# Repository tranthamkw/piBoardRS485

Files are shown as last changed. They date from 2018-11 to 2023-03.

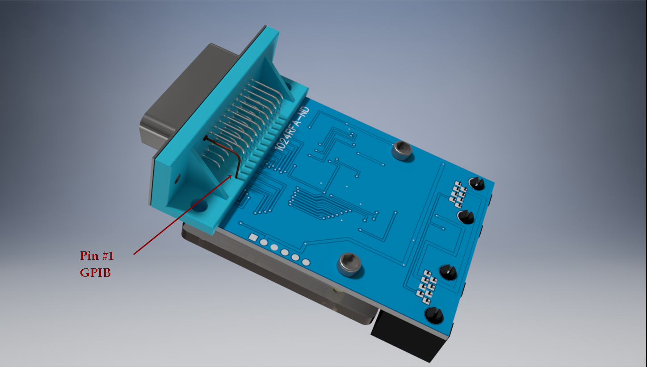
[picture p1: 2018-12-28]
GuestBoards/GPIB_Bridge/GPIB_Fmale_bottomview_Assembly.png

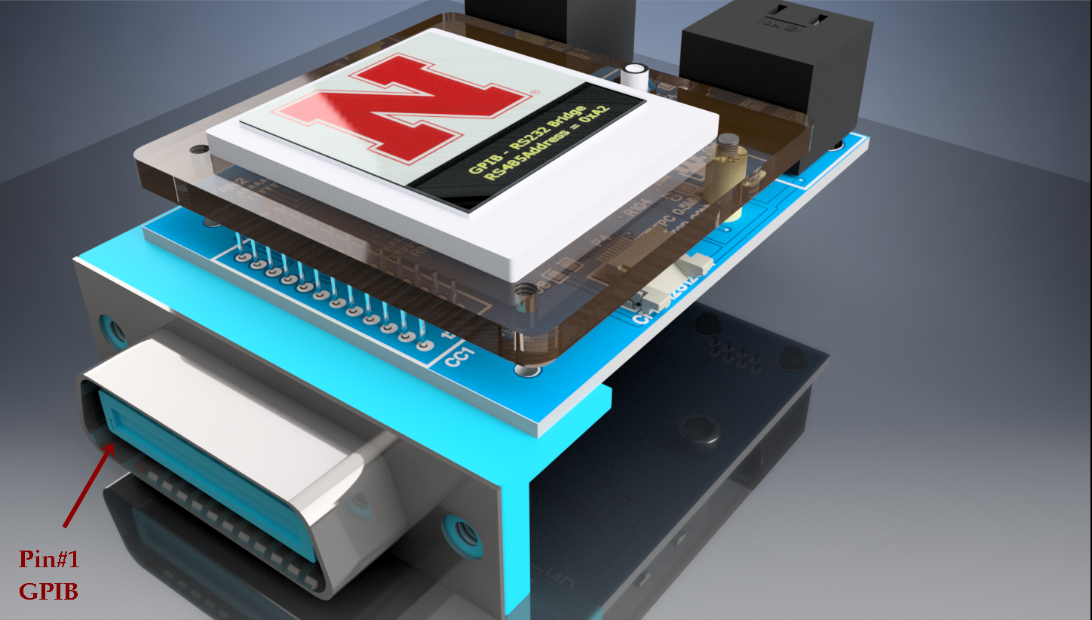
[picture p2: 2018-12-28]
GuestBoards/GPIB_Bridge/GPIB_Fmale_TOPview_Assembly.png

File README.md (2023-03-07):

# piBoardRS485
This repository provides the details of how to build a custom DAQ system based on the RS-485 communication protocol. The primary advantage to the RS-485 protocol is that it allows multiple devices to operate on a single communication line, and that single communication line is the commonly available ethernet cord. This line interfaces with other commonly used communciation standards and connectors, such as GPIB and RS-232, via custom circuit boards, which can be ordered online using the Gerber files located in this repository.

THe system was originally developed to be controlled by a RaspberryPi, but could work with other devices that support serial communication.

A full overview of the project is given in [the pdf document describing the project](https://github.com/tranthamkw/piBoardRS485/blob/master/PROJECTDESCRIPTIONUniversalDataAcq_RS485_system.pdf).

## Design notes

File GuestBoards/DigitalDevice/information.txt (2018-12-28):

/*

Digial devices:
A) servo control
B) General purpose digital IO
C) stepper motor control

Board is the same for all three devices. Funciton is determined with software. 

The  128x32 OLED display is optional. Devices do not require the display to function. Display functions could be removed from the compiled code. The display is useful for displaying routine information, such as the RS485 address. 

*/

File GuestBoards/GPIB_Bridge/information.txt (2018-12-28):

/*  GPIB bridge documentation

Two board versions:
1. Male GPIB uses connector like Digikey 1024RMA-ND mounted on the TOP side of the board. Note where pin 1 is. This version of the board does not have a pushbutton switch for changing the RS485 address.

2. Female GPIB uses connector like Digikey 1024RFA-ND mounted on the BOTTOM side of the board. Again, note where pin 1 is. This version of the board DOES have a push button. 

Both boards: the GPIB connector interferes with the the left two mounting holes for the plexiglass mounting plane for the LCD. The two right mounting holes are sufficient to hold the plexiglass.

*/

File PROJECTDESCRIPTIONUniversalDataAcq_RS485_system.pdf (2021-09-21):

A low‐cost, universal, open‐source, multi‐device data acquisition system for RS485, RS232,

GPIB, and analog devices.

K.W. Trantham and K.J. Ahrendsen

Abstract

A simple, and low cost computerized data acquisition system is presented. It is based on the

Raspberry Pi and can interface to a variety of new and legacy laboratory instruments. For

compatibility with the most common connection standards used by laboratory instruments

(GPIB, RS232, or analog output), it uses a network of communication bridges based on the

RS485 serial bus.

Introduction and motivation

Automated computer or microprocessor data acquisition (DAQ) systems have been in use for

small scale, “personal” experiments, since the 1970’s [1,2]. There are a number of data

acquisition systems, including both hardware and software, available primarily for Windows‐

based Personal Computers (PCs). Including the cost of the computer itself, these systems can be

quite expensive. Furthermore, such third‐party products are generally proprietary, and the

details of their DAQ systems, such as source‐code or electrical schematics, are not available to

the researcher. Over the last ten years, there has been an emergence of very low cost, single‐

board computers that are broadly open‐source, both in software and hardware.

Originally developed as a means to teach coding, the Raspberry Pi (RasPi) computer has many

general‐purpose input/output connections that make it ideal for laboratory automation tasks.

The RasPi uses an open‐source Linux‐based operating system. Furthermore, the vast majority

of software and hardware developed for the RasPi is also open‐source. However, given that the

RasPi is relatively new platform, there are few solutions available to connect it to stand‐alone

laboratory instruments such as an ammeter or lock‐in amplifier. Often, one has a collection of

operational legacy equipment, with much or all of it being unusable in a RasPi DAQ system

given the variety of connection standards. There are many examples [3‐7] where the RasPi has

found specific use in the research environment, often dedicated to a specific task. Herein we present a method for generally connecting the RasPi to any number of new and legacy

instruments, based on a universal, addressable data bus.

One of the most common laboratory instrumentation interfaces is the General Purpose Interface

Bus (GPIB), which conforms to the IEEE 488.1 standard.[8] This is an eight‐bit parallel bus, with

data management and handshake signals. The bus permits addressing up to 30 different

instruments interconnected to a host controller. This bus was first developed by Hewlett‐

Packard (HP) in the 1960’s and has continued to be the de facto standard in laboratory

instrumentation connectivity. To be used with a host computer (such as a PC) an interface card

must be installed. Data acquisition software can be written in native compiled languages, or in

graphical development environments such as LabView[9] or TracerDAQ[10]. Unfortunately, a

commercial solution does not exist to connect a Raspi to the GPIB. A new circuit directly

interfacing the Raspi to the GPIB was considered in the development of our data acquisition

system, but abandoned after considering other instrument connectivity issues.

Newer laboratory equipment may include a GPIB connection, but are more likely to include a

Universal Serial Bus (USB), or an RS232 serial connection. Developing software to communicate

over the USB to third party devices is problematic as special, proprietary drivers are often

required and may not be generally available. This became apparent in our group when trying

to interface to a HighFinesse Model WS‐6 wavemeter. The RS232 serial bus lends itself to

development of locally‐authored software as manufacturers will generally publish command

codes needed to operate their instrument. From an electronics point of view, interfacing the

Raspi to a RS232 bus is straightforward. However the RS232 bus is not addressable and permits

only one device to be connected to the DAQ computer at a time.

Given the diminishing use of GPIB [11] and the limitations of the RS232 bus, we consider the

RS485 serial communication bus. The RS485 bus, standardized in 1998 [12], is also a serial bus

like the RS232. However, the RS485 bus allows multiple devices to be on the same network.

Many modern industrial controls employ the RS485 bus, and its use is becoming more popular

in research settings[13‐17]. Herein we show how the RS485 bus can be used as an alternative,

universal instrumentation connection scheme for laboratory apparatuses. We show how to connect multiple legacy RS232 devices or GPIB devices with a communication bridge circuit. In

developing this bus, it was realized that other, simple interface devices could also be

constructed to expand the measurement and control capability of the laboratory data

acquisition computer.

The RS485 Bus as a Universal Data Bus

The RS485 communication standard defines potentials to represent logic states differently than

do the RS232 systems. Instead of dedicated “transmit” and “receive” potentials measured

relative to ground (three wires) as used in RS232, a version of the RS485 standard uses only two

wires with floating potentials not necessarily referenced to ground. Convention identifies the

two wires and associated potentials as A and B, and VA and VB respectively. Logic states are

determined by the potential difference between wire A and wire B; i.e the state equals the

difference VA ‐ VB. For example, if the difference is greater than zero this represents a logic 0,

and if it is less than zero it represents a logic 1. The advantage this scheme has over RS232

communications is that it is less susceptible to induced noise and completely immune to ground

loops. As a result, RS485 connecting cables can be longer than those for RS232.

To manage transmit and receive functions on the RS485 bus with only two wires, one must

adopt a half‐duplex communication approach. With this, all devices on the bus are by default

“listening” (receiving) with a very large Thevenin impedance seen at the A and B terminals.

Only one device on the bus can transmit at a time. The data conversation is initiated by a “host”

device such as the data acquisition computer. All other devices are then identified as “guest”

devices. In transmit mode, the host device has a very small equivalent Thevenin resistance and

is able to impose the appropriate potentials. The communication information must include an

address so that the appropriate guest device knows to respond when the host device has

completed transmission. After sending a message to the bus, the host enters a high impedance

state (receive mode) and awaits a response from the addressed guest device. The addressed

guest device, in turn, responds by transmitting data on the bus. Thus, the RS485 is an

addressable serial bus, in which there can be many guest devices attached to one host device.

The general architecture of the RS485 serial bus for this application is outlined in Figure 1. Since

the guest devices also require power to operate, +12V and ground are provided along with the

RS485 signals A and B. The electrical‐network connection between devices is simple parallel,

meaning that the network topology can be linear or forked. The RS485 standard does not

specify a physical connector. An RJ‐45 connector is used here, allowing up to eight independent

connections, however only two are used for communication and four more for power (two

wires for +12V and two wires for power ground). Since RJ‐45 is the physical connection

standard for Ethernet, a unique physical connector for this application would prevent

accidental connection of this bus to the Ethernet. However, this connection standard was

selected given the general availability of short “Ethernet cables” and the relatively low cost of

printed‐circuit‐board (PCB) mounted RJ‐45 connectors. The RS485 bus presented here should

not be plugged into an Ethernet connection.

The RS485 standard also does not specify how data is encoded. In this application, data is

encoded using a modified form of the Modbus protocol[18]. This specification outlines the

format of transmitting data, which includes a device address. Most importantly, the protocol

specifies a “cycle‐redundancy‐check” (CRC) to be appended at the end of each transmission.

The CRC is two bytes of data calculated based on the original message and is checked by the

receiver to ensure that there was not an error in transmission. When a guest device responds, in

addition to appending an appropriate CRC, its address is also transmitted so that the host

device can confirm that the correct device responded. Details of the data transmitted over the

RS485 bus are discussed below.

In the present application, there are two basic types of guest devices used. The first type is a

“bridge” device and there are two different versions. The first version is a RS485 to RS232

bridge. This circuit is different from commercially available RS232/RS485 converters, which

typically only modify voltage levels. The device presented here permits addressable

communication with an otherwise non‐addressable RS232 device. In this way, multiple RS232

enabled devices can be controlled with one host device. The second bridge device is a RS485 to

GPIB bridge. This permits a communication interface between the serial RS485 bus and parallel

GPIB bus. The second type of guest device presented is a variety of “general purpose” units

intended to perform simple measurement or manipulation tasks. All of these guest devices and

the host device, which attaches to a RasPi, is described in detail below.

Circuit Descriptions

All guest devices share required common elements in their circuitry. A schematic of these

elements is shown in Figure 2. Each device has two RJ‐45 connectors so that the bus may be

extended to more devices. As shown, pin connections 1 and 2 of the RJ‐45 carry the RS485

signals B and A respectively. Pins 7 and 8 deliver +12V power, with power ground on pins 3

and 4. Pins 5 and 6 are unused, and are tied together. A NCP117ST05T3G voltage regulator

(U2) provides regulated +5V for the guest device. The µMAX485 integrated circuit (U4) is a

data transceiver and provides the necessary electrical translation from RS485 differential

potentials A and B to the +5V, ground referenced transistor‐transistor‐logic (TTL) signals and

vice‐versa. Digital connection RE/DE of U4 determines the mode of communication. When

RE/DE is true, the device is in transmit mode, translating digital TTL level signals at input

UART_TX1 to the appropriate differential signals at A and B. When RE/DE is logical false, the

device is in receive mode and TTL data is provided to digital connection UART_RX1.

Momentary switch SW1 and resistor R2 provide a means to reprogram the device’s address.

This will be discussed further below.

All of the guest devices presented use a Microchip microcontroller (a “PIC”). The development

environment “MPLAB” is available at no cost from the manufacturer. The PIC is programmed

using a PICKIT4 programmer.[19] This low‐cost device connects to the guest board through the

In Circuit Serial Programming (ICSP) connection P1 as shown in Figure 2. Once the PIC is

programmed, the programmer is removed and the code remains on the microprocessor

indefinitely.

All guest devices share optional circuitry for displaying information locally, as shown in Figure

3. The RS232 and GPIB bridge devices use a 128x128 TFT display while all other general

purpose guest devices use a 128x32 OLED display. The displays chief purpose is to show the

user their unique RS485 address when turned on. Optionally, they can provide debugging information, such as the messages being carried from one bus to another as in the case for the

bridge devices. Only one connector and its associated display is used for a given device, but

both are shown in Figure 3. Both displays operate with +3.3V digital signals, and the circuitry

shown translates between this and the +5V logic used by the microcontroller of each device.

Dual transistor package Q101 contains two BSS138 field effect transistors. The operation of this

circuit as a logic level translation circuit is described in reference [20].

The RS485 to RS232 bridge circuit is shown in Figure 4. The indicated ports in Figure 4 connect

to the ports of the same name shown in Figures 2 and 3. The microcontroller U1 is a PIC

18F46K22 whose programming determines the overall behavior of the device. The code used on

all devices is freely available [21]. The 18F46K22 has two Universal Asynchronous Receive and

Transmit (UART) modules. The first UART module is connected to U4 (µMAX485) of Figure 2

and communicates with the RS485 bus. The second UART module is connected to U3

(MAX232) and communicates with the RS232 bus. As the female DB9 is commonly used on the

instruments that support RS232 communication, connector P3 in Figure 4 is a male DB9

intended to plug into the back of the instrument. Essentially, this bridge device listens on the

RS485 bus for data specifically addressed for it. When properly addressed through the RS485

bus, it strips out RS485 and Modbus specific data and transmits the intended message (usually

ASCII text) to the connected instrument via the RS232 bus. The bridge waits for a certain period

and transmits any data returned from the instrument back through the RS485 bus with

appropriate Modbus encoding data. Printed circuit Gerber files are also available [21].

The RS485 to GPIB bridge circuit is shown in Figure 5 and is similar in function to the RS232

bridge. It accepts properly addressed and encoded messages intended for a GPIB instrument,

passes along the instrument‐specific instructions, and returns any data passed back from the

instrument. This circuit only uses one UART of the microcontroller for the RS485 bus. The

GPIB communication is handled manually through the digital data Port A for reading and

writing data to the GPIB bus, while digital port D handles GPIB bus management signals per

IEEE 488.1. A full description of how the GPIB bus operates can be found in reference [22].

Briefly, the digital signals in the GPIB bus are “active low” meaning that a given signal is not true until the signal is near ground level. With many possible instruments on the bus, the signal

line will not be sensed low until all instruments have pulled the line low. The resistor networks

shown in Figure 5 permit the microcontroller to both sense the level of a given signal and

transmit data when needed.

Since the PIC microcontrollers have software‐controllable digital input/output ports as well as

analog input ports, we realized that RS485 devices could be constructed for simple remote data

acquisition and control tasks. Placing data acquisition and control tasks in a remote device frees

the main computer for other tasks. An example task that is better removed from the host

computer is the provision of regular step pulses to control a stepper motor. Because the RaspPi

runs a multitasking Linux operating system, like Windows on a PC, microprocessor time

dedicated to user code can be variable. This makes providing regularly timed pulses difficult.

A PIC microcontroller, on the other hand, runs dedicated code and timing functions can be

more precisely controlled with on‐chip counter‐timer circuits.

The electrical schematic for a general purpose RS485 digital guest device is shown in Figure 6.

This device can be programmed to control two servomotors, control one stepper motor, or

simply be a general‐purpose digital input/output device. Depending upon how the PIC is

programmed, output ports RA5 and RA4 of the PIC provide digital signals to control two

servomotors. Alternatively, these pins can output the pulse and clock signals for one stepper‐

motor, or, along with RC3 and RB4, can be used for general digital input/output (I/O) tasks.

The circuit is based on the PIC16F690 microcontroller. Like the PIC18F18K22, this

microcontroller is inexpensive and readily available. It has three 8‐bit general purpose digital

I/O ports, eight 10‐bit analog to digital converters (ADCs), two timers, two comparators, and

one UART. Many of these functions are tied to the same pin. For example, pin 12 of the

PIC16F690 is internally connected to digital port B bit 5, analog to digital converter channel 11,

and the receive connection for the UART. Therefore, the use of the pin must be configured in

software with the intended function. This means that other possible functions tied to a given

pin cannot be used at the same time. Connectors J4 and J5 provide power and signals for

conventional servo connectors. If this digital guest‐device is used as a servo controller, a separate voltage regulator U7 provides dedicated power for servos. Although the servos and

microcontroller circuit both require +5V to operate, the higher current drawn from the servos

can cause the supply voltage to fluctuate such that the microcontroller will reset. This generally

leads to erratic behavior.

Another use of the PIC16F690 as a remote RS485 guest device is to measure analog signals.

Some legacy equipment will only have an analog output as the remote sensing method. Figure

7 shows the schematic for a four‐input analog RS485 analog guest device. The analog input

section has a simple resistor and Zener diode network for limiting the input voltage to +5.1V

relative to ground as measured by the microcontroller. If the device needs to measure a

different voltage range, or bipolar voltages, then additional analog voltage conditioning circuits

can be added. The PIC16F690 uses a 10‐bit analog to digital converter (ADC). This resolution is

sufficient for many applications, however there are a variety of other PIC microcontrollers that

have better resolution or pre‐processing options such as averaging (see, e.g. the PIC18F27K42).

Finally, we present the circuitry for the host computer in Figure 8. The host computer is a

Rasberry Pi model 2 and connects to the circuit via connector P1. The circuitry is similar to the

guest devices in that a µMAX485 integrated circuit translates +5V TTL logic signals to RS485

potentials. The networks around Q1 and Q2 provide logic level shifting between the +5V

system of the µMAX485 and the +3.3V logic of the RasPi. There are two extra resistors attached

to the A and B wires of the RS485 bus. The A and B wires are completely floating and their

potentials could possibly drift outside of the 0 to +5V range used to power U4. These resistors

provide a minuscule amount of biasing current to prevent this. The main difference between

the RasPi host device and the other devices shown in previous figures is the software. The host

computer always initiates a data transfer by first addressing the intended device and then

awaiting a response. Although only two RJ‐45 connectors are shown in Figure 8, the user can

add as many connectors as needed. The RasPi computer can also interface to other devices

through the unused circuit node tags shown in Figure 8, e.g. CE0, MOSI, and WPi25. These are

not relevant to the RS485 host controller application and will not be discussed.

Data Format

The serial data format for all devices follows a modified form of the Modbus protocol. The

order of each 8‐bit byte has significance. The first byte transmitted by the host is the unique

RS485 address of the device which is intended to reply. This is followed by a control byte;

examples include 0x03 for reading from a register or 0x06 for writing to a register. The next two

bytes indicate which register to read from or write to. In the case of writing, the next two bytes

indicate what value to write. The last two bytes are the low and high order CRC bytes. As an

example, the byte stream

0xA1 0x03 | 0xF0 0xF2 <CRC_l> | <CRC_h>

transmitted by the host is intended for device number 0xA1 (decimal 161) and is requesting to

read data from register 0xF0F2. The host then goes into listen mode and awaits a response.

Only guest device 0xA1 will respond. The byte order of the response also has the address first,

and the second, control byte is echoed. In the case of writing to a register, the entire message is

typically echoed back. In the case of reading from a register, the third byte indicates the

number of bytes of data to follow in the stream. The low and high order CRC bytes are

transmitted last. Thus, continuing with the above example, the device might respond with five

bytes of ASCII encoded data for “HELLO” as,

0xA1 0x03 | 0x05 | 0x48 | 0x45 | 0x4C 0x4C 0x4F <CRC_l> | <CRC_h>.

All devices on the RS485 network employ a means of changing the RS485 address of the guest

device. This is necessary since all devices on the network must have a unique address between

0x00 and 0xFF. When the microcontroller is first programmed, the address is indeterminate.

All guest devices have an “ADDRESS” port to the microprocessor and associated momentary

switch. When the switch is held closed and a properly encoded message is sent at the same

time, the guest device will remember the address used in the message as its own and act on the

message. When the switch is released, this new address is permanently saved even if power is

removed from the device. A second method of changing the address is provided by software.

By sending the proper information through the RS485 bus to the correct register of the device,

the address can be changed as well.

An Example Use

We have adapted the digital host device to control laser paths on an optical table. It is a

straight‐forward procedure to connect a small flag to a servo. This allows the DAQ system to

block, or unblock a laser beam as desired. Further, a servo can be connected to a flip mirror for

controlling the laser beam direction. Referring to Figure 9, a small “fork” (item 4) is mounted

on a servo motor. An adjustable mirror mount (item2) [Thorlabs KM100] is mounted to a flip

mount adapter (1) [Thorlabs FM90]. The servo is mounted so that its axis is concentric with the

axis of the flip mount adapter. Finally, a protruding screw (item 3) in the mirror mount fits

between the tines of the fork.

Conclusion

We have presented a universal data acquisition bus to network a Linux‐based Raspberry Pi to a

variety of laboratory equipment. With communication bridges and general purpose RS485

devices, this system has been tested with a variety of devices. We have also developed a novel,

remote controlled flip‐mirror based on the general‐purpose digital device. Table 1 shows a

complete list of commercial equipment tested with our system and the mode of interface to the

RS485 bus. At any given time, all of this equipment can be connected to the bus and DAQ

computer.

Equipment | Mode of connection to RS485 bus
Keithley Model 485 Picoammeter | GPIB bridge
Keithley Model 617 Electrometer | GPIB bridge
Vortex Laser Model 6000 | RS232 bridge
Sacher Laser Head Controller PilotPC 500 | RS232 bridge
Sacher Tapered Amp Controller PilotPC 4000 | RS232 bridge
Omega Model CN7800 Temperature Controller | RS232 bridge
B&K Model 1696 power supply* | RS232 bridge
SRS Model SR830 Digital Lock‐in Amplifier | RS232 bridge or GPIB bridge
HighFinesse Model WS‐6 Wavemeter* | RS232 bridge
Grandville Phillips Model 307 ion gauge and Convectron gauge controller | Analog input guest device
FLUKE 8840 Multimeter | GPIB bridge
Sorensen 120‐0.5 power supply | GPIB bridge

Table 1. A list of commercial laboratory equipment tested and used with the described

RS485bus. Items marked with an asterisk have special notes, see text.

Interfacing to the Model WS‐6 wavemeter requires a special note. The hardware for this device

is controlled through the USB port with proprietary software written for the PC/Windows. The

software has a configuration option to continuously broadcast the wavemeter’s data through

the RS232 serial port of the PC. The above RS485 to RS232 bridge was adapted with a female

DB9 connector and wiring the Rx and Tx connections to the appropriate pins. The bridge was

reprogrammed to read two sequences of the byte stream from the PC computer since, at any

given moment when the data was requested from the DAQ host, the first data sequence could

be incomplete. The B&K Model 1696 power supply can also connect directly through RS485.

However, its mode of communication is ASCII text only. To preserve the purity of the

communication on the RS485 bus and to avoid possible data errors with other devices using the

Modbus data format, the RS232 bridge is used with this power supply.

The components used on each device and the host computer are relatively inexpensive. It is

straight‐forward to connect the RasPi to the RS485 bus since TTL‐level serial Rx and Tx

connections are readily available. This universal system of connecting multiple devices can be

extended to using a PC as the DAQ. In this extension, however, a translation circuit such as a

RS232 to RS485 bridge would need to be employed as TTL connections are not available on the

PC.

Acknowledgements

This work was supported by the NSF through Awards PHY‐1505794 and PHY‐1806771.

References

1. D.W. Taylor, Review of Scientific Instruments 49, 1551 (1978).
2. Douglas Whiting, Review of Scientific Instruments 55, 1157 (1984).
3. Alfredo Benítez, Ulises Santiago, John E. Sanchez, and Arturo Ponce, Review of Scientific

Instruments 89, 013702 (2018).

4. F. Arnold, I. DeMallie, L. Florence, and D. O. Kashinski, Review of Scientific Instruments 86,

035112 (2015).

5. James Keaveney, Review of Scientific Instruments 89, 035114 (2018).
6. Matthew G. Street, Cristin G. Welle, and Pavel A. Takmakov, Review of Scientific

Instruments 89, 094301 (2018).

7. N. B. Clayburn, K. W. Trantham, M. Dunn, and T. J. Gay, Review of Scientific Instruments 87,

124903 (2016).

8. IEEE Standard Digital Interface for Programmable Instrumentation, Institute of Electrical and

Electronics Engineers, 1987, ISBN 0‐471‐62222‐2,

9. See www.ni.com/labview for LabVIEW.
10. See https://www.mccdaq.com for TracerDaQ.

11 J Ryland ‐ Autotestcon, 2005. IEEE, 2005 ‐ ieeexplore.ieee.org, DOI:

10.1109/AUTEST.2005.1609228

12. Electronic Industries Alliance standard ANSI/TIA/EIA‐485‐A‐1998.
13. J. Vega, A. Mollinedo, A. López, L. Pacios, and S. Dormido, Review of Scientific Instruments

68, 963 (1997).

14. A. K. Sanyasi, R. Sugandhi, P. K. Srivastava, Prabhakar Srivastav, and L. M. Awasthi,

Review of Scientific Instruments 89, 055113 (2018).

15. Hui Gao, Qiuping Wang, Weibin Wang, Qinglin Wu, Wentong Chen, Liusi Sheng, and

Yunwu Zhang, Review of Scientific Instruments 72, 3979 (2001)

16. Sanjeev R. Kane, Chander Kant Garg, and R. V. Nandedkar, AIP Conference Proceedings

879, 635 (2007)

17. R. Szplet, P. Kwiatkowski, K. Różyc, Z. Jachna, and T. Sondej, Review of Scientific

Instruments 88, 125101 (2017).

18. http://www.ni.com/white‐paper/7675/en/ for Introduction to Modbus (white paper).
19. See https://www.microchip.com for PICkit programmers and MPLAB software.
20. Phillips AN10441 application note https://www.nxp.com/docs/en/application‐

note/AN10441.pdf

21. Schematics, microcontroller source code, and circuit board Gerber files available at [URL

held pending anonymous peer review] github repository.

22. See http://www.ni.com/white‐paper/3389/en/ for Introduction to GPIB messages (white

paper)

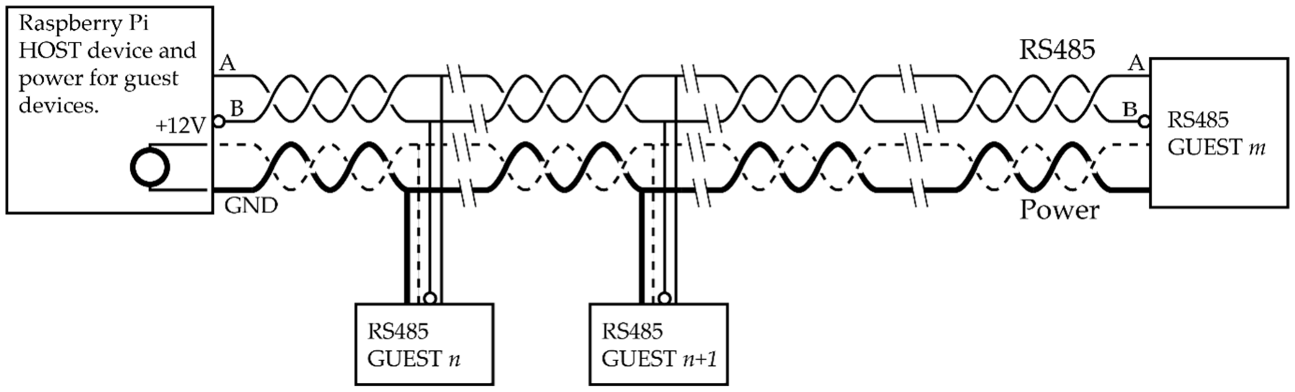
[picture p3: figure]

Figure 1. General architecture of the powered RS485 instrumentation bus.

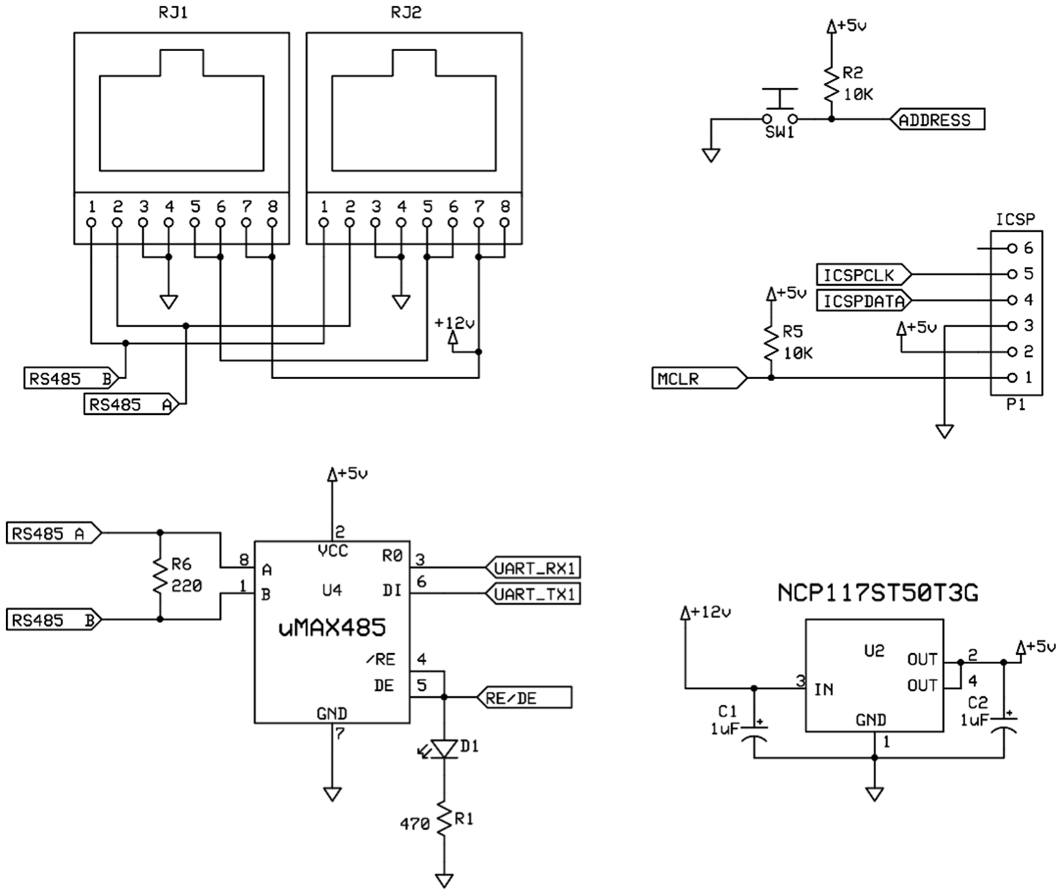
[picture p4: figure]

Figure 2. Schematic of the required common elements found in each guest RS485 device.

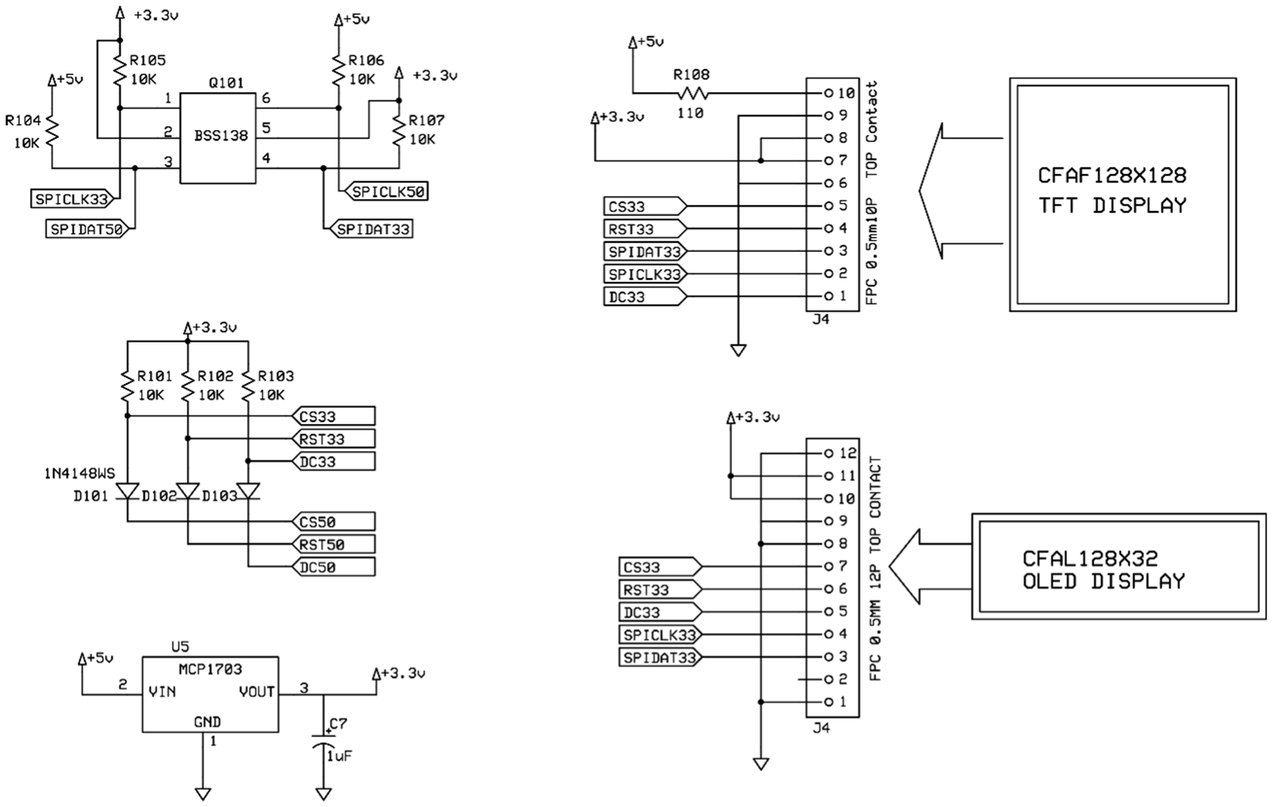
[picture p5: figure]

Figure 3. Schematic of optional display circuitry used on each device. The bridge guest devices

use the 128x128 TFT display, while all other devices use the 128x32 OLED display.

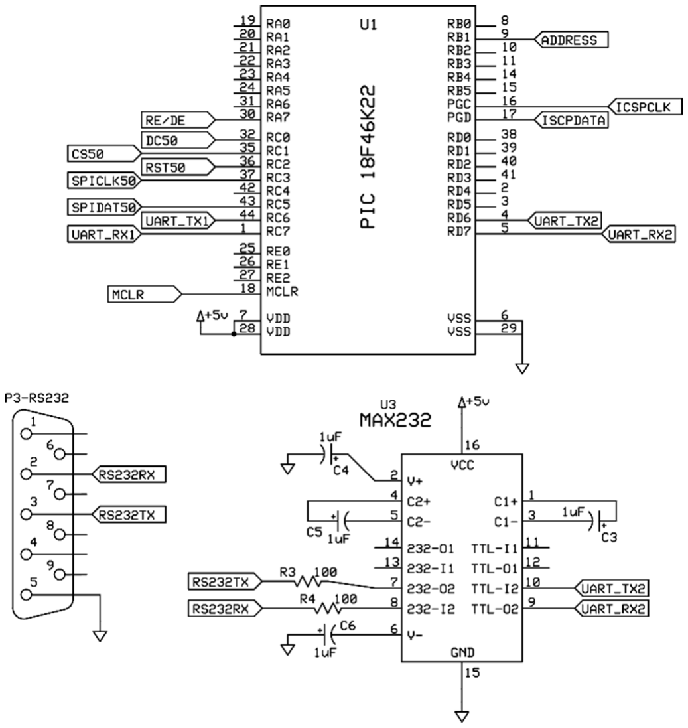
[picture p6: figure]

Figure 4. Schematic of RS485 to RS232 bridge guest device.

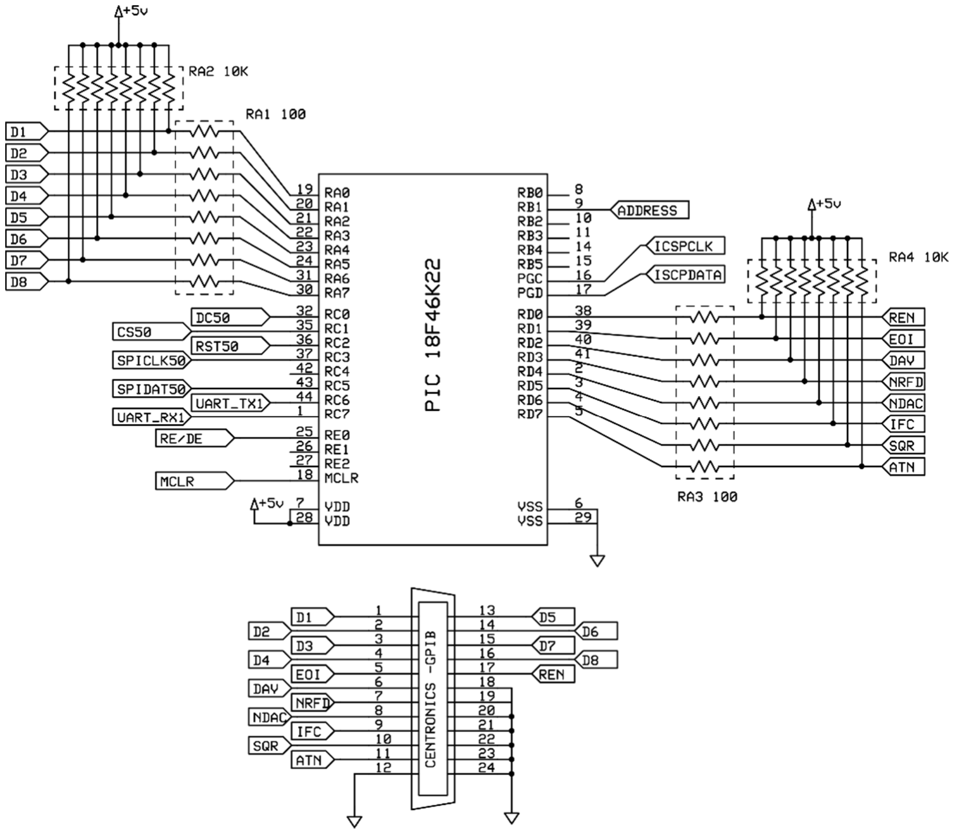
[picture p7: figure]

Figure 5. Schematic of RS485 to GPIB bridge guest device.

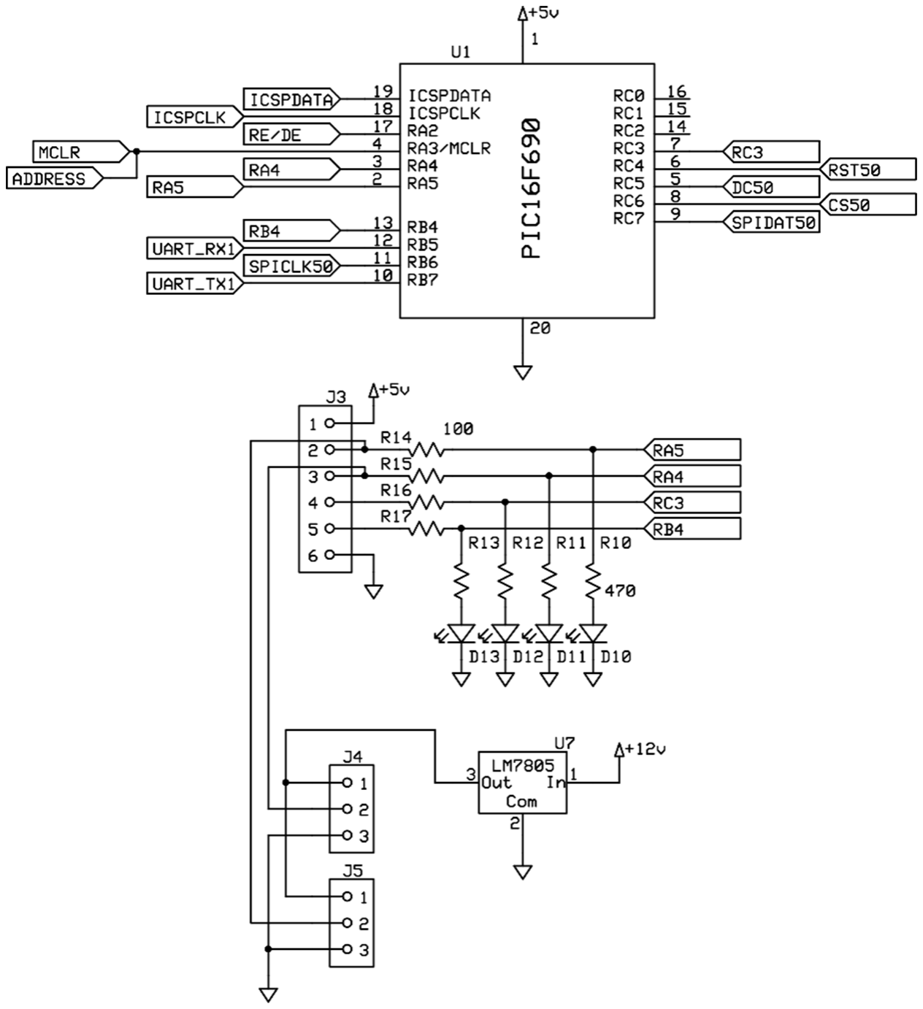
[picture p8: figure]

Figure 6. General‐purpose digital RS485 guest device. With appropriate software, this circuit is

used to control two servomotors, one stepper motor, or provide general digital I/O signals.

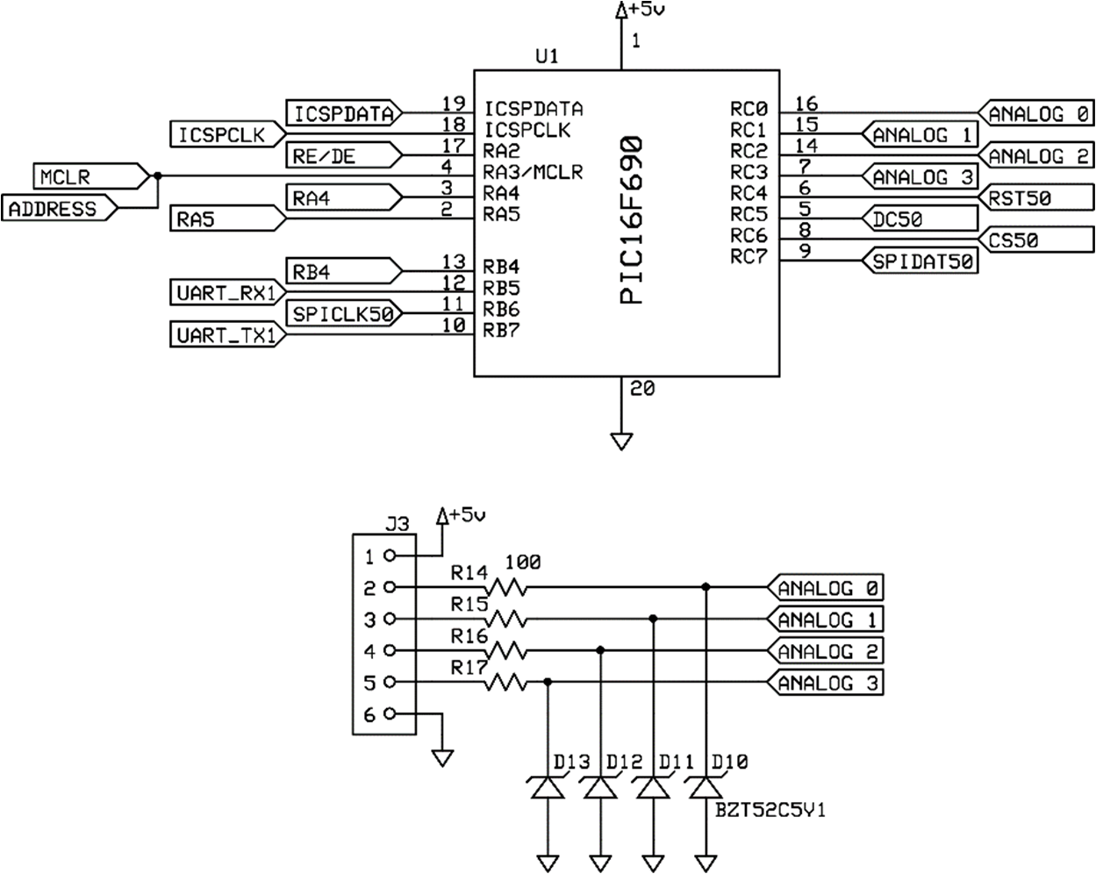
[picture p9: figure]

Figure 7. General‐purpose analog input RS485 guest device.

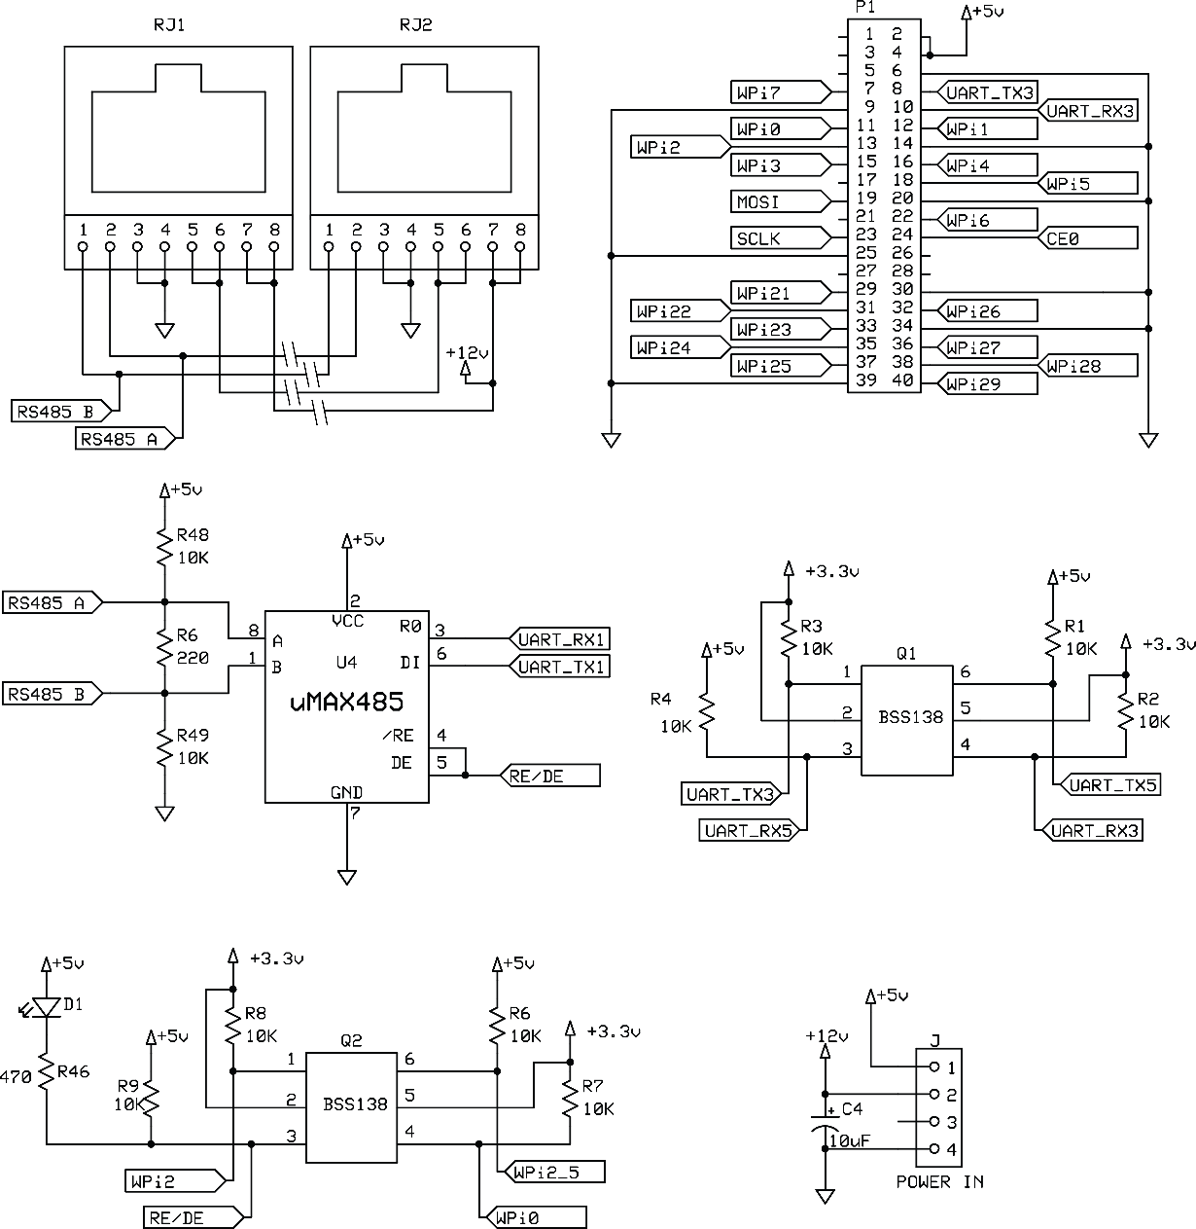
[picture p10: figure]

Figure 8. Circuit for the raspberry Pi RS485 host controller.

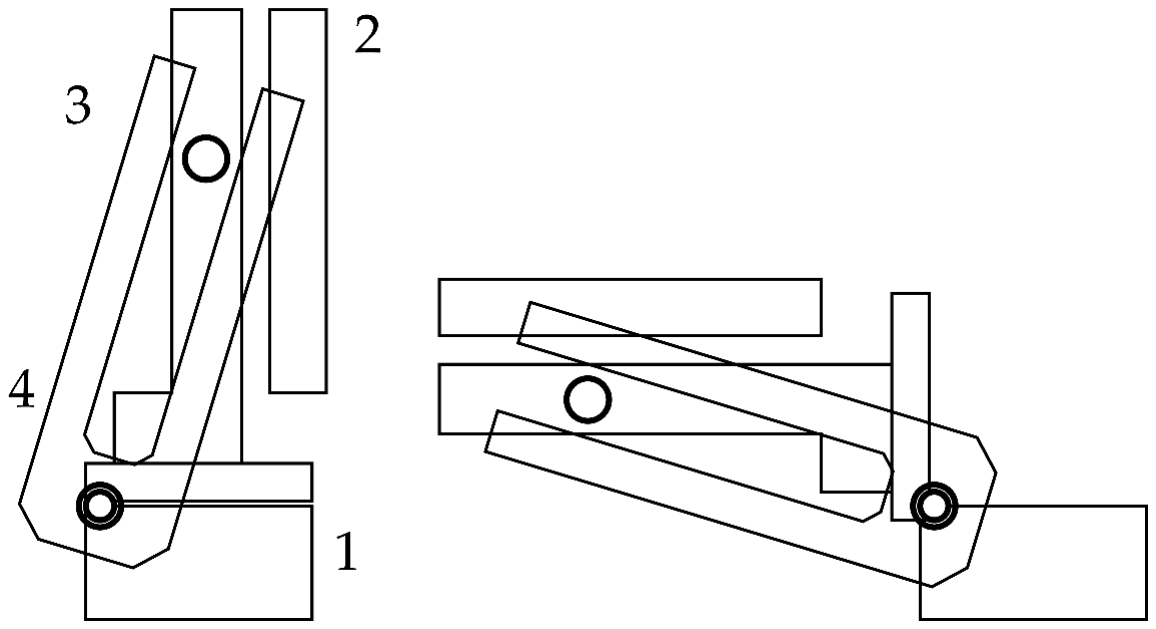
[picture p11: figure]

Figure 9. An automatic flip‐mirror based on the digital servo guest device. A servo (not

shown) is used to change the position of a mirror. See text for numbered item descriptions.

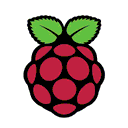
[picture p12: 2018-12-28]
RaspPi128x128.bmp

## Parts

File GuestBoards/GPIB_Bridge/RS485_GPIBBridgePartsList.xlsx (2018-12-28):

Name | Designator | Footprint | Quantity | Supplier | Supplier Part
1uF | C7,C1,C2 | CASE-A_3216 | 3 | https://www.digikey.com | 399-3680-1-ND
GPIB_connector_male | CC1 | 24-p.085" pitch FEMALE | 1 | https://www.digikey.com | 1024RFA-ND | <- with 20181111200508 board
 | CC1 | 24-p.085" pitch MALE | 1 | https://www.digikey.com | 1024RMA-ND
1N4148WS | D101,D102,D103 | SOD-323-F | 3 | https://www.digikey.com | 1N4148WSFSCT-ND
LTST-C170KRKT | LED1 | LED-0805 | 1 | https://www.digikey.com | 475-1278-1-ND
Header-Female-2.54_1x6 | P1 | HDR-6X1/2.54 | 1 | https://www.digikey.com | 732-5339-ND
FPC 0.5MM 10P Pull type H2.0mm Pick up | P4 | FPC-0.5MM-LSSJ-H2.0-10P_TOP | 1 | https://www.digikey.com | HFK110CT-ND
BSS138DW-7-F | Q101 | SC-70-6(SOT-363) | 1 | https://www.digikey.com | BSS138DW-FDICT-ND
470Ω(471) | R1 | 0603' | 1 | https://www.digikey.com | 311-470CRCT-ND
10K | R105,R104,R106,R107,R102,R101,R103 | 0805' | 7 | https://www.digikey.com | 311-10.0KCRCT-ND
120R | R108 | 0805' | 1 | https://www.digikey.com | 311-120CRCT-ND
10K-0805 | R2,R5 | 0805' | 2 | https://www.digikey.com | 311-10.0KCRCT-ND
220R-1206 | R6 | 1206 | 1 | https://www.digikey.com | YAG5046CT-ND
RJ45c | RJ1,RJ2 | RJ45-3.68 | 2 | https://www.digikey.com | 553-2264-ND
ResistorArray100 | RN1, RN3 | RESISITOR_ARRAY_742C163_CTS | 1 | https://www.digikey.com | 742C163101JPCT-ND
ResistorArray10k | RN2,RN4 | RESISITOR_ARRAY_742C163_CTS | 3 | https://www.digikey.com | 742C163103JPCT-ND
SWITCH,6*6*9PLASTIC HEAD,260G, 0.25MM,SMD | SW1 | SMD-6X6X9 | 1 | https://www.digikey.com | EG4356CT-ND
PIC18F46K22-I/PT | U1 | TQFP-44_10X10X08P | 1 | https://www.digikey.com | PIC18F46K22-I/PT-ND
NCP1117ST50T3G | U2 | TO-261-4 | 1 | https://www.digikey.com | NCP1117ST50T3GOSCT-ND
MAX485CUA+ | U4 | UMAX-8 | 1 | https://www.digikey.com | MAX485CUA+-ND
MCP1703AT-3302E/MB 3.3V Regulator | U5 | SOT-89(SOT-89-3) | 1 | https://www.digikey.com | MCP1703AT-3302E/MBCT-ND
128x128 1.45" Full Color TFT LCD Display | *not shown | Mounts external | 1 | https://www.crystalfontz.com | CFAF128128B10145T

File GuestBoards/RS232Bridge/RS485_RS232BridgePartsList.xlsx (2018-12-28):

Name | Designator | Footprint | Quantity | Supplier | Part number
1uF | C1,C2,C3,C4,C5,C6,C7 | CASE-A_3216 | 7 | https://www.digikey.com | 399-3680-1-ND
1N4148WS-E3-08 GP DIODE | D101,D102,D103 | SOD-323-F | 3 | https://www.digikey.com | 1N4148WSFSCT-ND
LTST-C170KRKT | LED1 | LED-0805 | 1 | https://www.digikey.com | 475-1278-1-ND
Header-Female-2.54_1x6 | P1 | HDR-6X1/2.54/rightAngle | 1 | https://www.digikey.com | 732-5339-ND
RS232-DB9 | P3-RS232 | PCB Edge mount | 1 | https://www.digikey.com | 209ME-ND
FPC 0.5MM 10P Pull type H2.0mm TOP | P4 | FPC-0.5MM-LSSJ-H2.0-10P_TOP | 1 | https://www.digikey.com | HFK110CT-ND
BSS138DW-7-F | Q101 | SC-70-6(SOT-363) | 1 | https://www.digikey.com | BSS138DW-FDICT-ND
470R | R1 | 0603 | 1 | https://www.digikey.com | 311-470CRCT-ND
10k | R2,R5,R104,R105,R106,R107,R102,R101,R103 | 0805 | 9 | https://www.digikey.com | 311-10.0KCRCT-ND
120R | R108 | 0805 | 1 | https://www.digikey.com | 311-120CRCT-ND
100R | R3,R4 | 0805 | 2 | https://www.digikey.com | 311-100CRCT-ND
220R | R6 | 1206 | 1 | https://www.digikey.com | YAG5046CT-ND
RJ45c | RJ1,RJ2 | RJ45-3.68 | 2 | https://www.digikey.com | 553-2264-ND
SWITCH,6*6*9PLASTIC HEAD,260G, 0.25MM,SMD | SW1 | SMD-6X6X9 | 1 | https://www.digikey.com | EG4356CT-ND
PIC18F46K22-I/PT | U1 | TQFP-44_10X10X08P | 1 | https://www.digikey.com | PIC18F46K22-I/PT-ND
NCP1117ST50T3G | U2 | TO-261-4 | 1 | https://www.digikey.com | NCP1117ST50T3GOSCT-ND
MAX232ESE+T | U3 | SOIC-16_150MIL | 1 | https://www.digikey.com | 296-14619-1-ND
MAX485CUA+ | U4 | UMAX-8 | 1 | https://www.digikey.com | MAX485CUA+-ND
MCP1703AT-3302E/MB 3.3V Regulator | U5 | SOT-89(SOT-89-3) | 1 | https://www.digikey.com | MCP1703AT-3302E/MBCT-ND
128x128 1.45" Full Color TFT LCD Display | *not shown | Mounts external | 1 | https://www.crystalfontz.com | CFAF128128B10145T

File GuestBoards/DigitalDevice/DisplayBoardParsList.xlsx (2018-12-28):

Name | Designator | Footprint | Quantity | Supplier | Supplier Part
BSS138DW-7-F | Q1 | SC-70-6(SOT-363) | 1 | Digikey | BSS138DW-FDICT-ND
10k-0805 | R1,R2,R3,R4,R5,R6,R7 | 0805' | 7 | Digikey | 311-10.0KCRCT-ND
1N4148WS-E3-08 GP DIODE | D1,D2,D3 | SOD-323-F | 3 | Digikey | 1N4148WSFSCT-ND
MCP1703AT-3302E/MB 3.3V Regulator | U1 | SOT-89(SOT-89-3) | 1 | Digikey | MCP1703AT-3302E/MBCT-ND
1uF | C1 | CASE-A_3216 | 1 | Digikey | 399-3680-1-ND
FPC_0.5MM_12P_rEVERSE | P4 | FPC-0.5MM-LSSJ-H2.0-12P | 1 | Digikey | A100294CT-ND
Header-Female-2.54_1x8 | P1 | HDR-8X1/2.54 | 1 | Digikey | 732-5321-ND
128x32 I2C Graphic OLED Module with ZIF Connector |  |  | 1 | www.crystalfontz.com | CFAL12832D-B

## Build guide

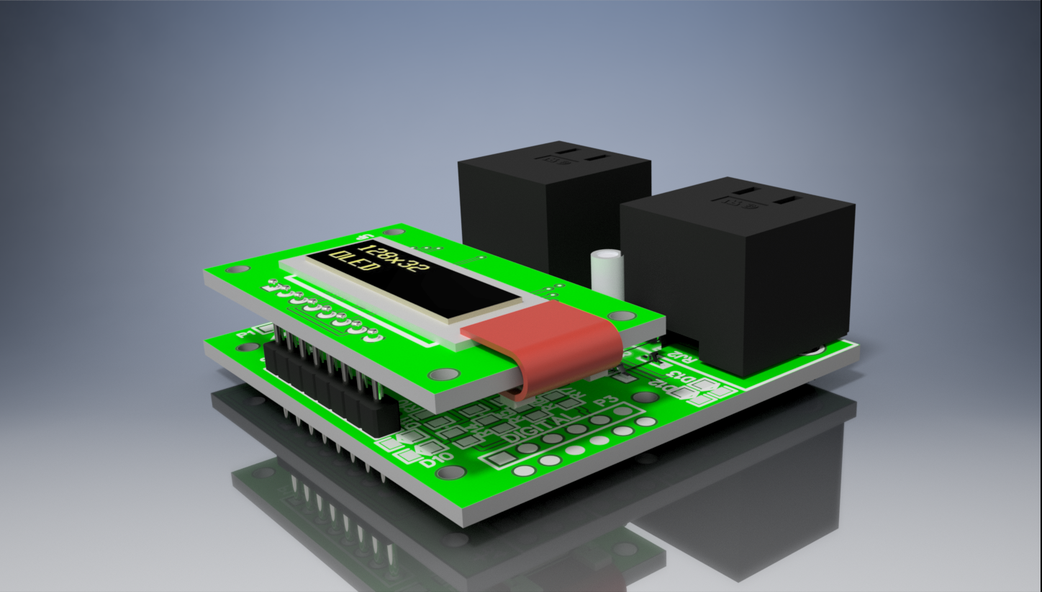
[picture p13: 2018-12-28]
GuestBoards/DigitalDevice/DigitalBoardAssembly.png

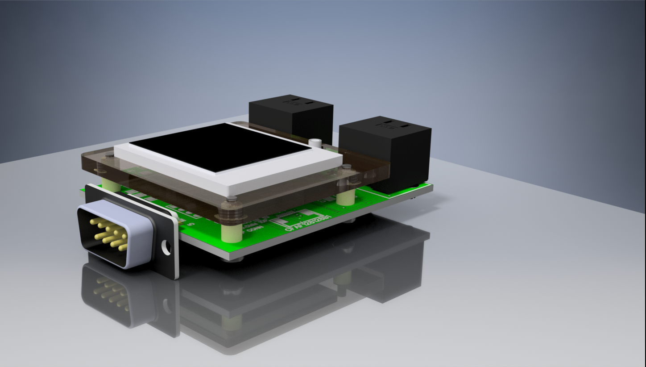
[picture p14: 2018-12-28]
GuestBoards/RS232Bridge/RS232Bridge_assembly.png

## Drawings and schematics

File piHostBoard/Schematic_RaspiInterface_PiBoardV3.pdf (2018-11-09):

+12V +5V
+5V

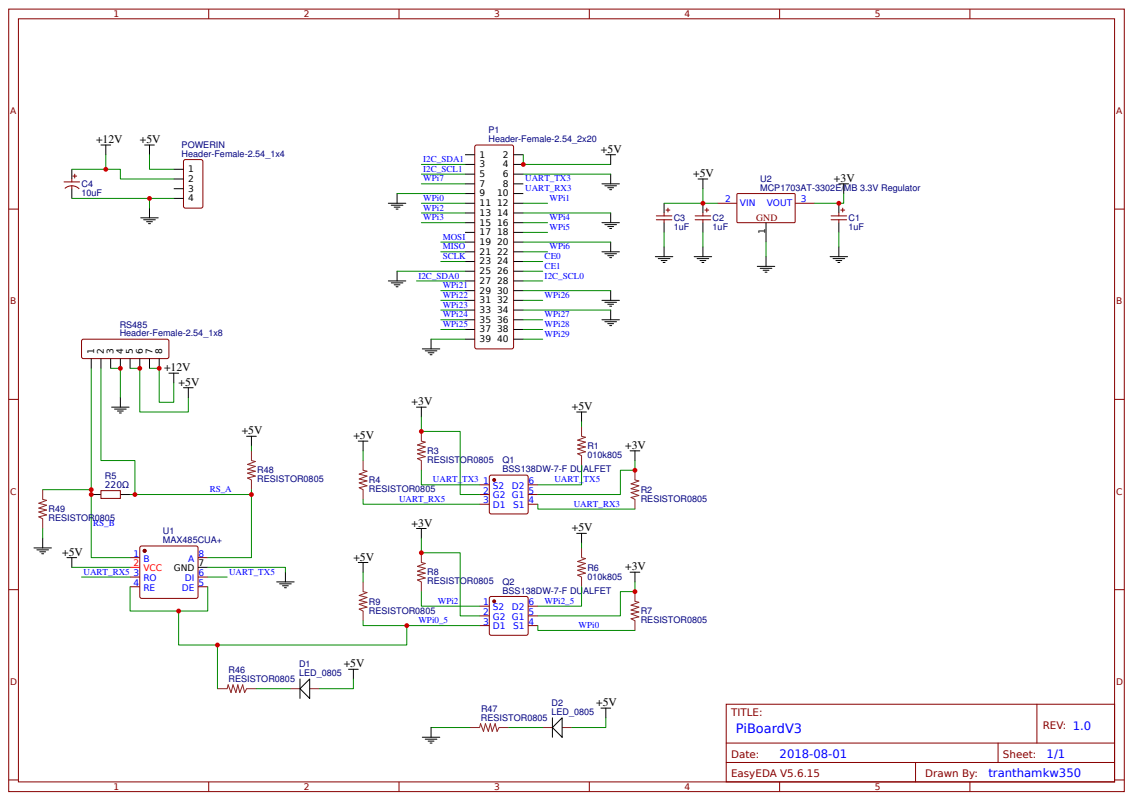
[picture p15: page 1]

+5V

+5V

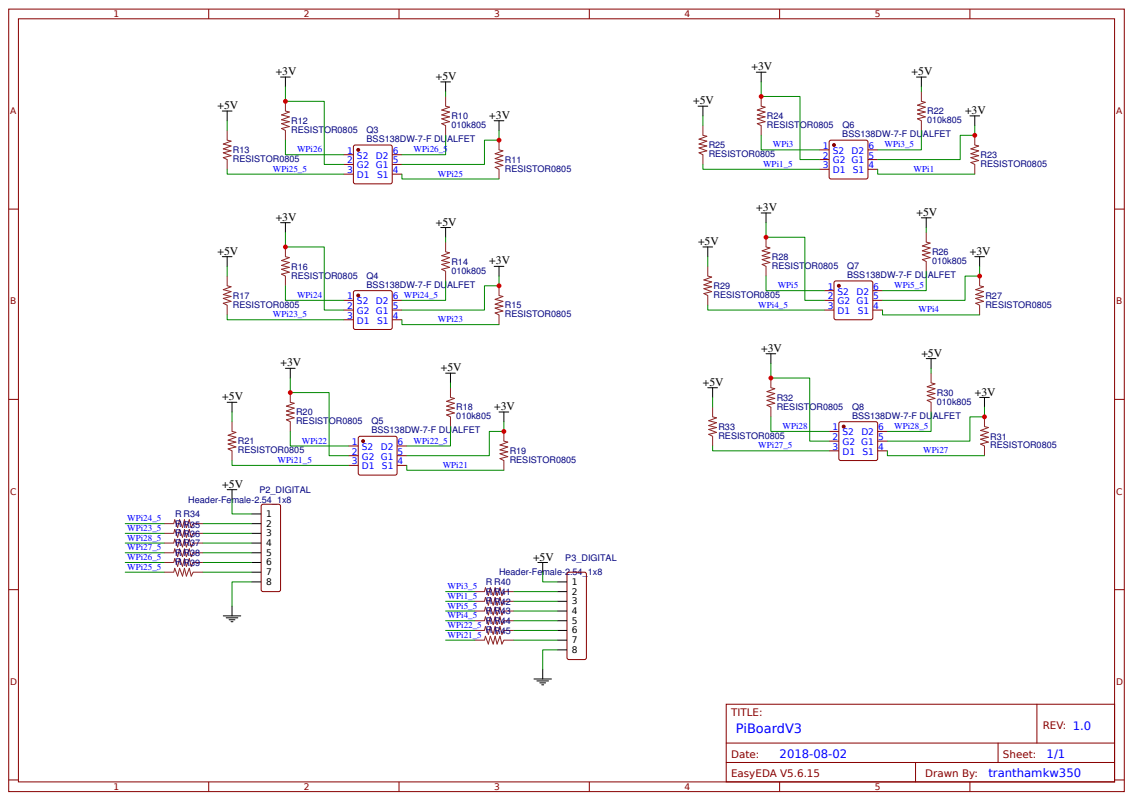
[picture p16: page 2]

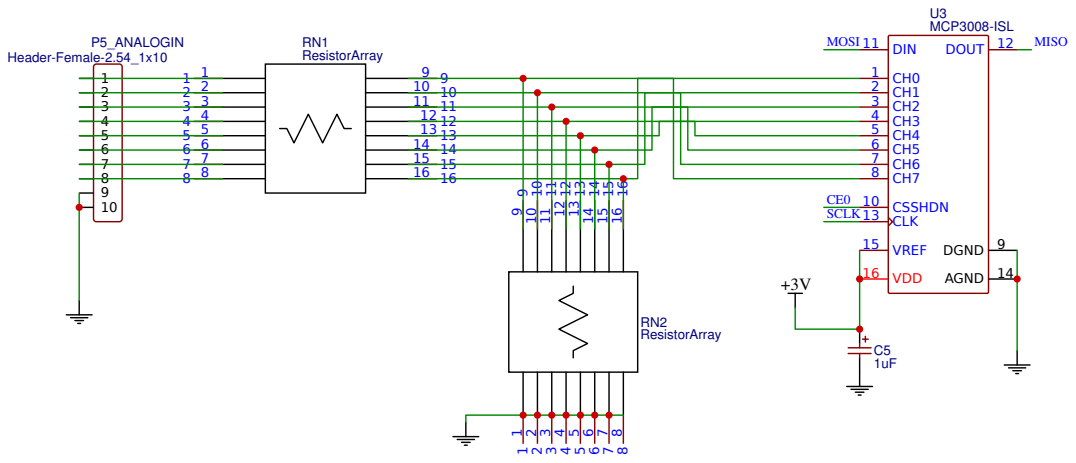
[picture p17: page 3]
TITLE:; New Schematic; REV: 1.0; Date:; Sheet: 1/1; MCP3008-ISL; DGND 9; CSSHDN 10 CLK 13; VREF 15; DIN 11; DOUT 12; AGND 14 VDD 16; Header-Female-2.54_1x10; P5_ANALOGIN; CE0 SCLK; MOSI; MISO; ResistorArray

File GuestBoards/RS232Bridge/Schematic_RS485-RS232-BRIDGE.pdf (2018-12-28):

+5V

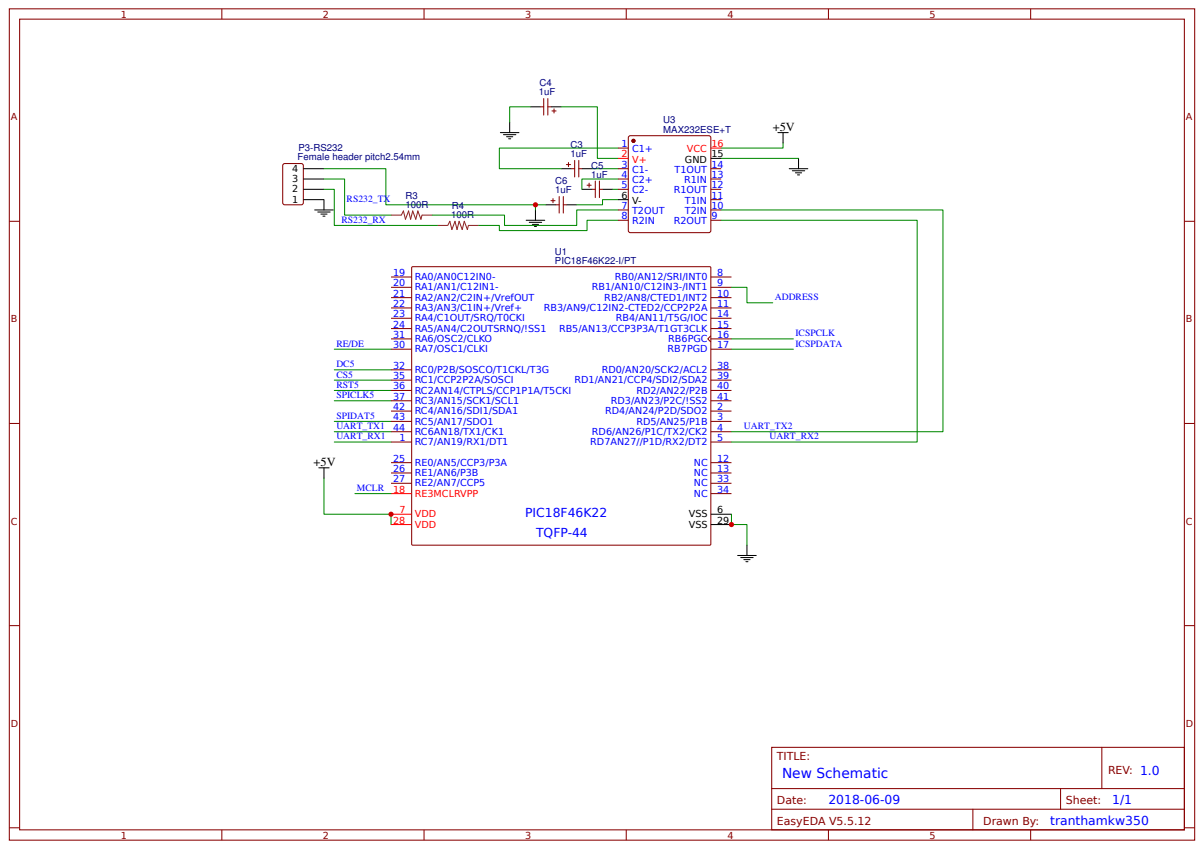
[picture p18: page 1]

+5V
+5V

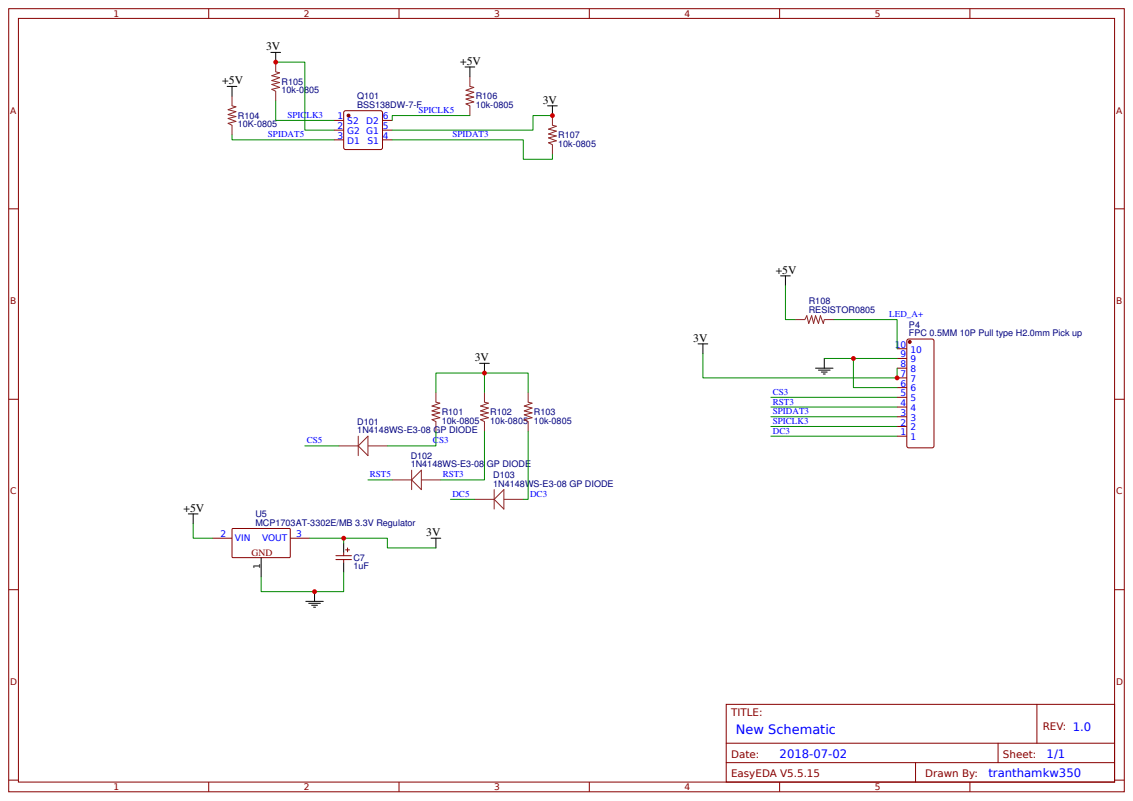
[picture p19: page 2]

+5V

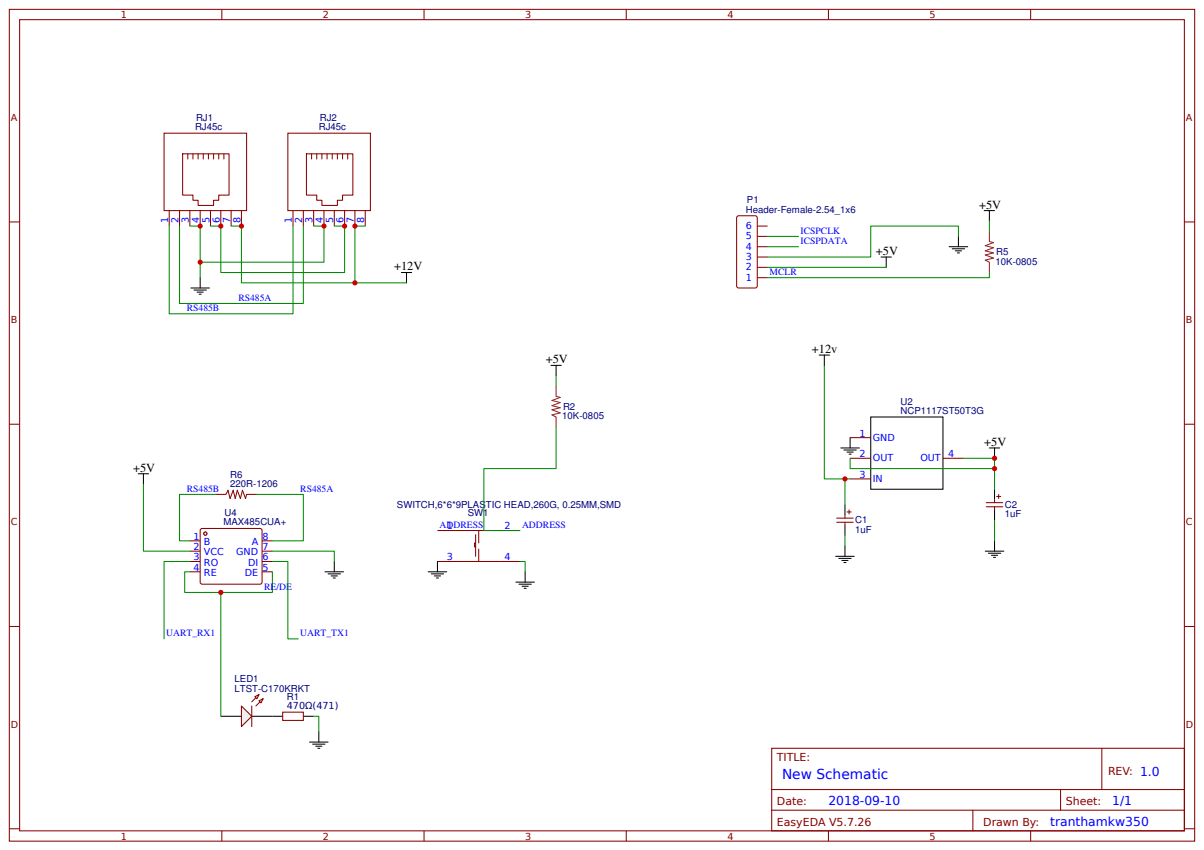
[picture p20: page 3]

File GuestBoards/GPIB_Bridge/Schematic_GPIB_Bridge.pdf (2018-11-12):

+5V

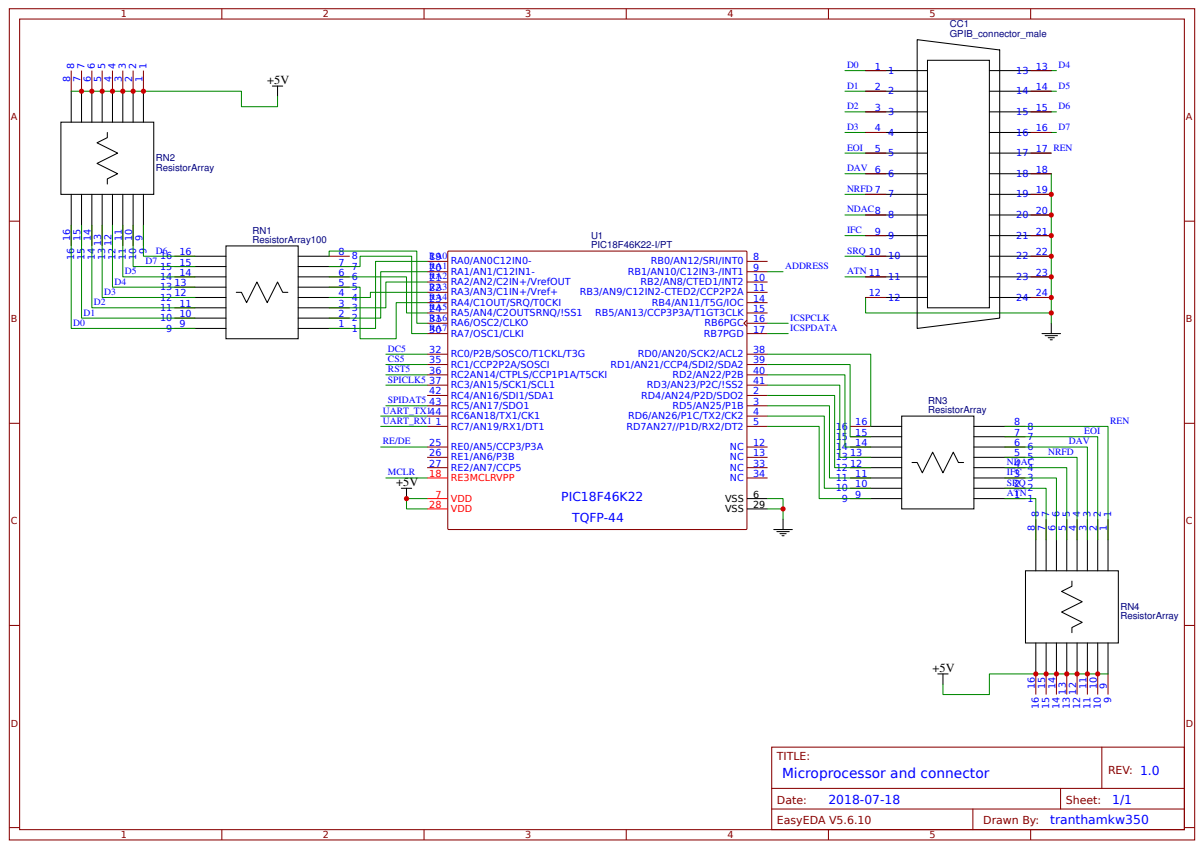
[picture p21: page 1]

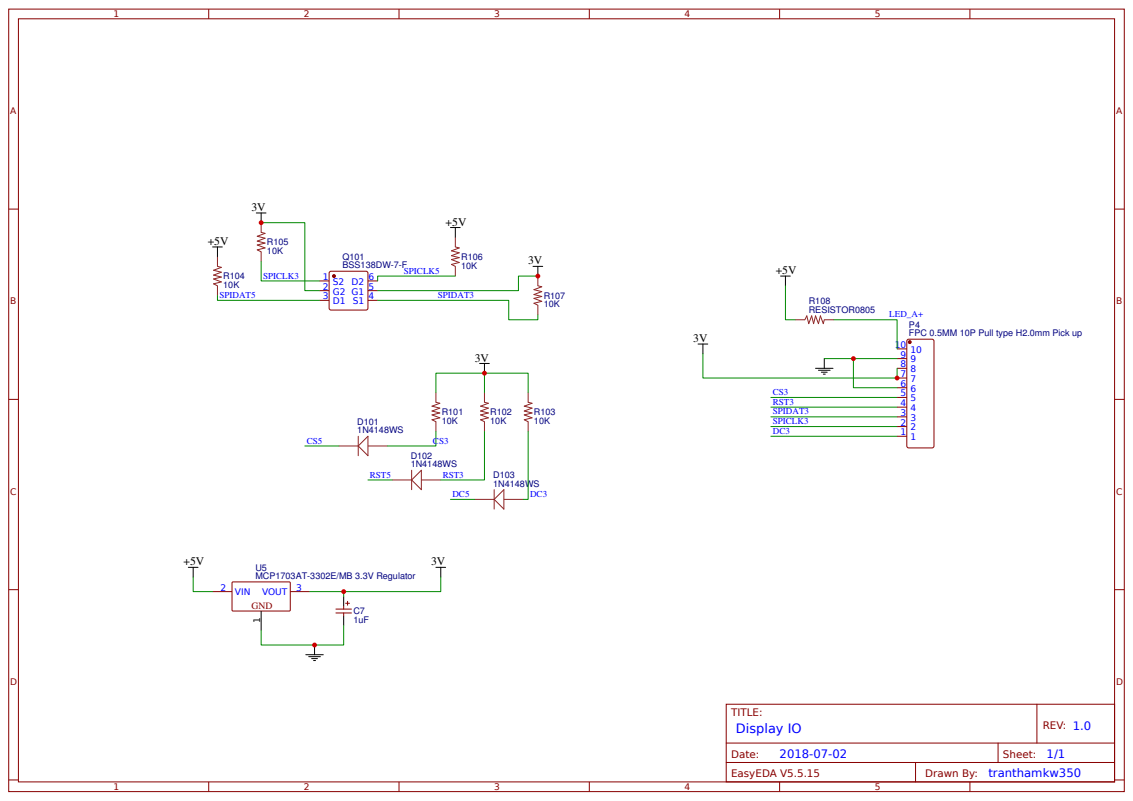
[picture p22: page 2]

+5V

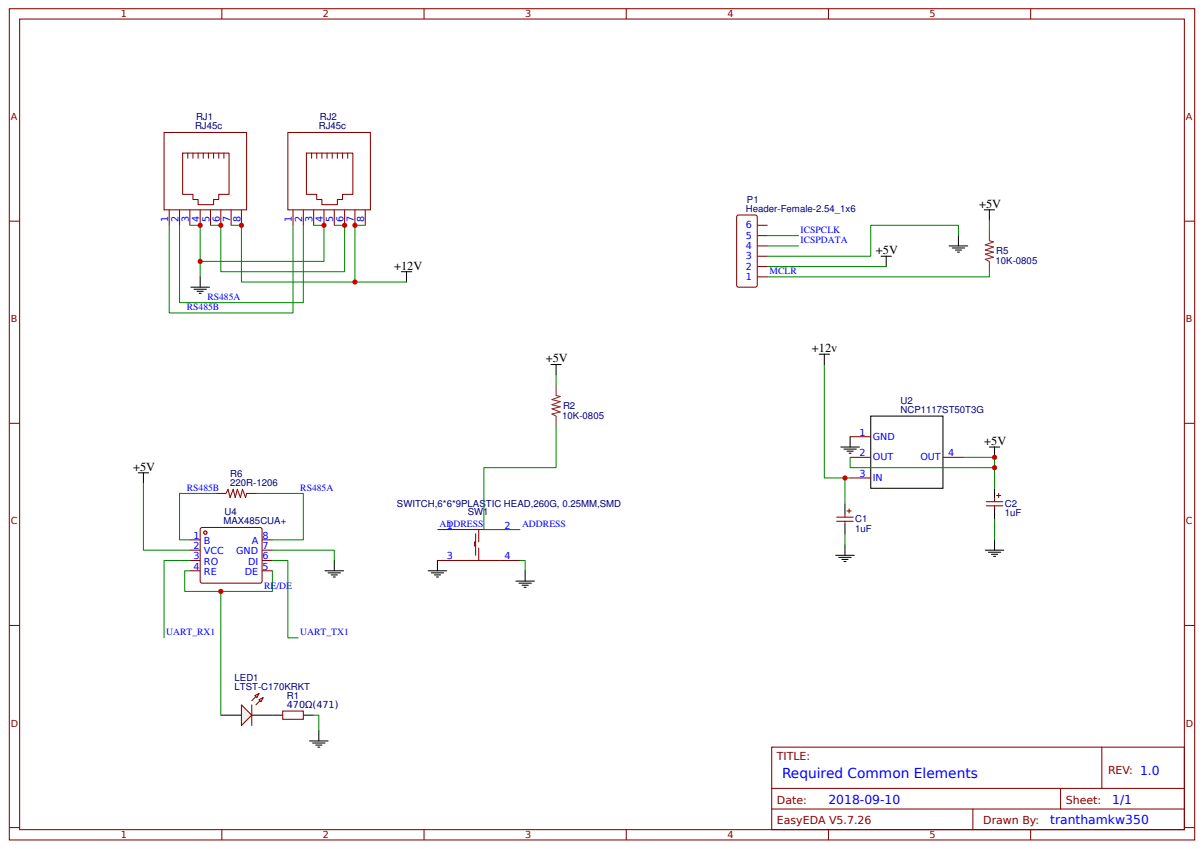
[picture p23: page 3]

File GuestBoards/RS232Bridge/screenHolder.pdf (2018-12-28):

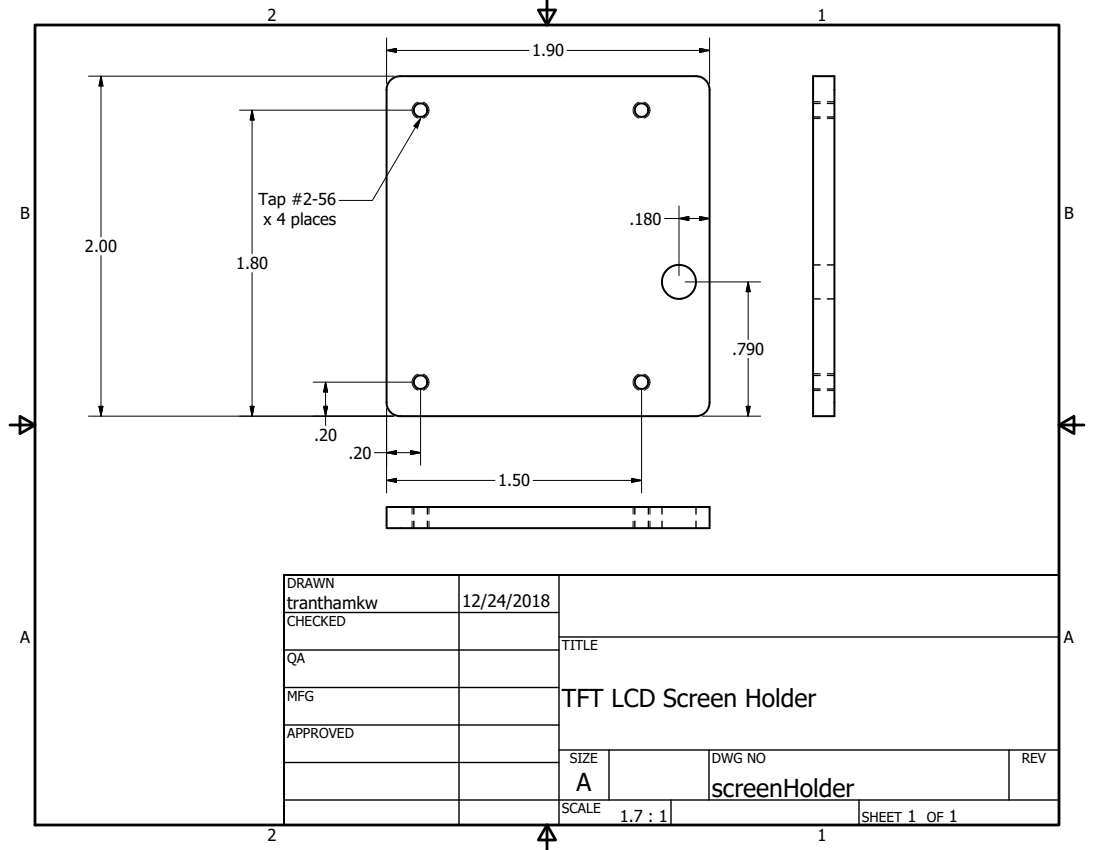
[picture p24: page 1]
Tap #2-56 x 4 places

DRAWN tranthamkw | 12/24/2018

CHECKED

TITLE
TFT LCD Screen Holder

MFG

APPROVED

SIZE A | DWG NO screenHolder | REV

SCALE 1.7 : 1 | | SHEET 1 OF 1

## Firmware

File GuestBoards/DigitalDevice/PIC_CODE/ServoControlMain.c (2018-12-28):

#include <pic.h>
#include <string.h>
#include "ModBusRTU.h"
#include "SSD1306.h"


/*

Microcontroller listens to RS485 commands and sets one of two servos to one of 8 positions. 

Set Servo to one of eight positions:
Write 
<RS485Address> 06 0A 0A 00 <pos> <CRCh> <CRCl>
with <pos> in the range 0 to 8

Responds with echo, or shows error in byte[1]

*/

__CONFIG(INTIO & WDTDIS & PWRTEN & MCLRDIS & UNPROTECT & BORDIS &
IESODIS & FCMDIS);

#define BASEREG 0x0A0A
#define FNREG 0x00F0
#define MAX_COUNT 200
#define MYFUNCTION "DUAL SERVO"
unsigned char address=0xA0;

unsigned char time_count=0;  
unsigned char servo1_count=10;  //counts number of 0.1mS.  Minimum is 10. Maximum is 20
unsigned char servo2_count=15;

void updateDisplayStatus(void){
	char temp[16],outText[24];
	unsigned int k;
	clearDisplaySSD1306();
	strcpy(outText,"FUNCTION: ");
	strcat(outText,MYFUNCTION);
	k=strlen(outText);
	writeCharSSD1306(0,0,outText,k,0);

	strcpy(outText,"RS485Address: 0x");
	itoa(address,&temp,16,2);
	strcat(outText,temp);
	k=strlen(outText);
	writeCharSSD1306(1,0,outText,k,0);

	strcpy(outText,"SERVO 1: ");
	itoa(servo1_count-10,temp,10,2);
	strcat(outText,temp);
	k=strlen(outText);
	writeCharSSD1306(2,0,outText,k,0);


	strcpy(outText,"SERVO 2: ");
	itoa(servo2_count-10,temp,10,2);
	strcat(outText,temp);
	k=strlen(outText);
	writeCharSSD1306(3,0,outText,k,0);

}


static void interrupt isr(void)
{
  if(T0IF) {	            // TIMER0 Interrupt Flag
	time_count++; // counts the number of times we go through this interupt. This interrupt is called every 0.1 mS
    /* MAX_VALUE=200  */
    if (time_count == MAX_COUNT) { //reset everything and turn on 
		RA5=1;
		RA4=1;
      	time_count=0;
        }
    if (time_count == servo1_count) {
		RA5=0;
      }
	if (time_count == servo2_count) {
		RA4=0;
      }
    TMR0 = 180;             // Initial Value for 0.1ms Interrupt
    T0IF = 0;		    // Clear TIMER0 interrupt flag
  }
}

void main (void) {	
 	int i,k;
	int reg;
	int strlength;
	char error;
	char data[24];
	char fnString[16];
	unsigned short outdata;
	
	PORTA =0;    //clears port A
	TRISA=0;
	TRISC = 0;    
	PORTC = 0;    //clears port C
	CM1CON0 = 7;    //turn off comparators
	CM2CON0 = 7;
	CM2CON1 = 7;
	ANSEL = 0;    //turns off ADC
	OSCCON=0x70;         // Select 8 MHz internal clock
	address=EEPROM_READ(0x00);

   OPTION = 0b00000000; // 1:2 Prescaller
  TMR0=180;            // Interupt every 0.1 ms
  T0IE = 1;		       // Enable interrupt on TMR0 overflow
  GIE = 1;		       // Global interrupt enable
	strlength=0;
	error=0;

	RS485_Init();
 	initSSD1306();
	updateDisplayStatus();


  do  {

	if (RS485_Data_Ready()==1){
			strlength = RS485_Read_Data(data,24);
			CREN=0;	
			if (validateRTU(data,strlength) ==0){
					// RTU CRC valid
					if (!RA3) {	// if button pressed, remember this address as our own.
						address = data[0];
						EEPROM_WRITE(0x00,address);
					}
					delay(300);
					if (data[0]==address){ //address byte
							// message intended for us
						switch (data[1]){  // command code byte
				
							case 0x06: // write a register
								reg = (data[2]<<8) | (data[3]);
									switch (reg){
									case BASEREG:
										outdata =(data[4]<<8)| data[5];  // assign new data to varible ("register")
										if (outdata<9){
											servo1_count=outdata + 10;
											// formulate a response echo back command
											strlength=6;
											RS485_Write_Data(data,strlength);
											error = 0;
												}else {
												error = 0x06; // out of range
												}
										break;
									case (BASEREG+1):
										outdata =(data[4]<<8)| data[5];  // assign new data to varible ("register")
										if (outdata<11){
											servo2_count=outdata + 10;
											// formulate a response echo back command
											strlength=6;
											RS485_Write_Data(data,strlength);
											error = 0;
												}else {
												error = 0x06; // out of range
												}
										break;
									case FNREG:
										if (data[4]==address){
											address=data[5];
											EEPROM_WRITE(0x00,address);
											strlength=6;
											RS485_Write_Data(data,strlength);
										} else {
										error = 0x02;
										}
									break;
									default:
										// invalid register
										error = 0x02;
										break;
										}
								break; // write to a register
							case 0x03:  // read a register
								reg = (data[2]<<8) | (data[3]);
								switch (reg) {
										case BASEREG:
											outdata = (unsigned short) servo1_count;
											outdata-=10;
										// formulate a response. 
											data[2]=2;  //number of bytes to follow of data
											data[3]=(outdata&0xFF00)>>8; //MSB first
											data[4]=(outdata&0x00FF);
											strlength=5;
											RS485_Write_Data(data,strlength);
											error =0;
											break;
										case (BASEREG+1):
											outdata = (unsigned short) servo2_count;
											outdata-=10;
										// formulate a response. 
											data[2]=2;  //number of bytes to follow of data
											data[3]=(outdata&0xFF00)>>8; //MSB first
											data[4]=(outdata&0x00FF);
											strlength=5;
											RS485_Write_Data(data,strlength);
											error =0;
											break;
										case FNREG:
											strcpy(fnString,MYFUNCTION);
											strlength = strlen(fnString);
										//data[0]=<RS485Address>; //data[1]=03;
											data[2] = (unsigned char)strlength;// number of bytes to follow
											for (i=0;i<strlength;i++){
												data[3+i]=fnString[i];
											}
											strlength+=3;
											RS485_Write_Data(data,strlength);
											error =0;
											break;
										default:
										error = 0x02; // invalid register
										break;
								}		
							break;// read a register
						
							default:
								// unknown command byte
								error = 0x08;
							break;
						}//end switch
						if (error) {
								data[1]=data[1] | 0x80;
								data[2]= (error & 0xFF00)>>8;
								data[3]=(error & 0x00FF);
								strlength=4;
								RS485_Write_Data(data,strlength);
						}
					updateDisplayStatus();
					}/// message intended for another address. ignore message.
			}else {
					//invalid RTU  just ignore the message
			}

			CREN=1; // this sequence resets the receive register. The act of writing tends to load a single bit 
			CREN=0;
			CREN=1;
		}// end data ready
 
}while(1);
}

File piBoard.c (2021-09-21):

#include "piBoard.h"

// ADC variables
#define BASE 100
#define SPI_CHAN 0
#define RS485CONTROL 0
#define BAUD 9600
#define LISTEN 0
#define WRITE 1

// wiring pi GPIO pin assigments to stepper motor drivers

void delayMicrosecondsHard(unsigned int howLong);
int initialize_rs485(void);


int fd;

// these are for RS485 communications

long int calcDelay(int size){
	long int del;
	// calculate the delay needed. for RS485 communications. depends on the number of chars we are transmitting
	del=size*10*1000000;
	 /* (10=8bits+2parity)  bits per character  *  1000000 microseconds per second
		  8 bits per char plus start and stop bits. 
		Tested watching an O-scope with 4 to 10 input chars. */
	del=del/BAUD; // * 1 second per baud 
return del;
}

void delay_uS(int x){

delayMicrosecondsHard(x);

}

int initializeBoard(){

	if (wiringPiSetup () == -1) 
	  {
	    fprintf (stdout, "Unable to start wiringPi: %s\n", strerror (errno)) ;
	    return 1 ;
	  }

	mcp3004Setup(BASE,SPI_CHAN);// for ADC
	initialize_rs485();

return 0;
}

int initialize_rs485(void){

  if ((fd = serialOpen ("/dev/ttyAMA0", BAUD)) < 0)
  {
    fprintf (stderr, "Unable to open serial device: %s\n", strerror (errno)) ;
    return 1 ;
  }
	pinMode(RS485CONTROL,OUTPUT);
	digitalWrite(RS485CONTROL,LISTEN);
	return 0;
}//end initialize



int closeBoard(){
	serialClose(fd);
return 0;
}



int getADC(unsigned short chan, unsigned int * returndata){
/*
uses MCP3004 chip attached to SPI channel 0 of RasPi GPIO
this chip has 8 analog inputs, chan 0 ... 7
returns value 0 to 1023
*/

int x;
	x=analogRead(BASE + chan);
	*returndata=x;
return 0;
}


int write_Modbus_RTU(unsigned short address, unsigned short reg, unsigned int writedata){
	unsigned char cmd[64];
	unsigned char returndata[64];
	short temp;
	unsigned int len,j,z;
	cmd[0]=address;
	cmd[1]=0x06; //command to write register(s)
	cmd[2]=((reg&0xFF00)>>8); //MSB which register
	cmd[3]=(reg&0x00FF); //LSB which register 

	temp=(unsigned short)writedata;
	cmd[4]=((temp & 0xFF00)>>8);// the next two bytes are the MSB and
	cmd[5]=(temp & 0x00FF);	  // and LSB of the data to send
	len=6; // count them

	temp = modRTU_CRC(cmd,len);//calculate the crc bytes. temp is 16bit, two byte value

	cmd[len+1]=(unsigned char)((temp&0xFF00)>>8);  //ensures that the MSByte is sent first as per Modbus
	cmd[len]=(unsigned char)(temp&0x00FF);  //before the LSByte

	write_rs485BYTE(cmd,len+2, returndata, &j);// this is a generic 'write data to RS485'
			// it assumes nuthing about the communication standard

	z=-1; // initialize an error variable.
	if(validateRTU(returndata,j)==0){	//CRC valid.No transmission errors
		// let make sure no machine/interpretation  errors
		if(cmd[0]==returndata[0]){  // then the corect machine responded
			if (returndata[1] & 0x80){ // then an  error
				z=returndata[2]; //in the event of an error this byte
			// is sent by the machine  explaining the nature of the error
			}else{
			 z=0;  // no errors. you're golden.
			} 
		}
	}
	return z;
}



int read_Modbus_RTU(unsigned short address, unsigned short reg, unsigned int* cnReturnData){
	/*
	   This layer packs together a Modbus style command to read messages. they 
	   are send to rs485 communication
	   any  returned data is placed in cnReturnData. 
	   */
	/*
	unsigned char cmd[64];
	unsigned char returndata[64];
	unsigned short temp;
	unsigned int  tempint;
	*/
	unsigned char cmd[64];
	unsigned char returndata[64];
	short temp;
	int  tempint;
	unsigned int len,j,z,numbytes;
	//build a Modbus RTU style command message to send 
	cmd[0]=address;
	cmd[1]=0x03; //command to read register(s)
	cmd[2]=((reg&0xFF00)>>8); //MSB which register
	cmd[3]=(reg&0x00FF); //LSB which register  to start from
	cmd[4]=0x00;//MSB how many
	cmd[5]=0x01;//LSB how many registers to read...   just one, thank you very much
	len=6; // count them. length of command

	temp = modRTU_CRC(cmd,len);//calculate the crc bytes

	cmd[len+1]=(unsigned char)((temp&0xFF00)>>8);  //ensures that the MSByte is sent 
	cmd[len]=(unsigned char)(temp&0x00FF);  //before the LSByte

	write_rs485BYTE(cmd,len+2, returndata, &j);
	/* len is the  number of input bytes in the command to send. Add two for the CRC bytes
	   and send ALL these bytes.  returndata holds any response */
	z=-1; //my way of recording errors
	tempint=0;

	if(validateRTU(returndata,j)==0){	/* this checks the last
										   two CRC bytes to ensure
										   transmission is  valid.*/

		if(returndata[0]==cmd[0]){ // then the correct machine responded
			if(returndata[1] & 0x80){// then an error occured
				z=(returndata[2]<<8)|returndata[3];
			}
			else{ 
				/*All good lets do something with the data.
				 *
				 * The return structure looks like 
				 * byte0: echo address
				 * byte1: echo command. If command is 03, then 03 is expected. However, if 
				 * there is an error it will return 83
				 * byte2: number of bytes of data to follow: n. 
				 * byte3: data byte 0.... 
				 * byte3+n: data byte n-1
				 * byte 3+n+1: LSB of CRC
				 * byte 3+n+2: MSB of CRC
				 * 
				*/
				numbytes=returndata[2];

				for (j=0;j<numbytes;j++){
					tempint+=(returndata[3+j] << (8*(numbytes-1-j)));
				}
				z=0;
				*cnReturnData=tempint;
			}
		}
	}
	return z;
}



unsigned short modRTU_CRC(unsigned char* buff, unsigned short len){
//calculates CRC for Modbus specs
	unsigned short crc=0xFFFF;
	unsigned short pos, bit;

	for(pos=0;pos<len;pos++){
		crc^=(unsigned short) buff[pos];
		for(bit=8;bit!=0;bit--){
			if((crc&0x0001)!=0){
				crc>>=1;
				crc^=0xA001;
			}else{
				crc>>=1;
			}
		}
	}
return crc;
}


int validateRTU(unsigned char* buff, unsigned short len){
	/* len is the full length of the buffer.  The last two elements in the array
	are assumed to be  CRC bytes.
		*/
	int j;
	unsigned short temp;
	j=-1;
	if(len>3){
		temp=((buff[len-1]<<8)|(buff[len-2]));
		if(temp==modRTU_CRC(buff,len-2)) j=0; // valid.yes.
	}
return j;
}



void write_rs485BYTE(unsigned char* cmd, unsigned int numchar, unsigned char* pszEcho, unsigned int* sizeEcho){

	unsigned int i,j;
	unsigned int loop;

	digitalWrite(RS485CONTROL,WRITE);// sets the control signal WRITE to the RS 485 buss
	delayMicrosecondsHard(20);// minor wait to allow signals to settle

	for (j=0;j<numchar;j++){
		serialPutchar(fd,cmd[j]);
	}
	// cannot read in from UART until done transmitting, so wait . . . 
	delayMicrosecondsHard(calcDelay(numchar+3));

	digitalWrite(RS485CONTROL,LISTEN);// now set control to READ (i.e. LISTEN)
	loop=0;
	j=0;
	do {
		delay(100);
		i=0;
		while (serialDataAvail(fd)){
		    while (serialDataAvail (fd)){
			pszEcho[i]=serialGetchar(fd);
			i++;
	    		}
			delay(70);
		}
		if (i>0) loop=100;
		loop++; j++;
	} while(loop<100);
	//debug printf("number of loops %d,j);

	*sizeEcho=i;
}

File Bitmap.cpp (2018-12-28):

/*
 * bitmap routines
 *
 * Only deal with 24 bit bitmaps.
 *
 *   general formula for getting pixel info
 *  int i=(col+(rows*(mywidth)))*3 + rows*offset;

    red = pB->data[i+2];
    green = pB->data[i+1];
    blue = pB->data[i];

 */


#include "Bitmap.h"

// put this in RRGGBB format
unsigned int Bitmap::getPixel(int row, int col){
    unsigned char red, green, blue;
    red = 0;
    green = 0;
    blue = 0;
    if ((row<height)&(col<width)&(row>0)&(col>0)){

       int i=(col+(row*(width)))*3 + row*(padWidth - byteWidth);
       red = data[i+2];
       green = data[i+1];
       blue = data[i];
    }
  return (red<<16|green<<8|blue);
}

void Bitmap::setPixel(int row, int col, char red, char green, char blue){
     if ((row<height)&(col<width)&(row>0)&(col>0)){
       int i=(col+(row*(width)))*3 + row*(padWidth - byteWidth);
       data[i+2]=red;
       data[i+1]=green;
       data[i]=blue;
    }
}

//basic constructor
Bitmap::Bitmap(){
    reset();
}


// constructor to make an empty bmp of size width X height X bpp
Bitmap::Bitmap(int newwidth, int newheight, unsigned short newbpp){
        reset();
    width=newwidth;
    height=newheight;
    bpp=newbpp;
     // bpp must be 24.
    //calculate the witdh of the final image in bytes
    byteWidth=padWidth=(width*3);
    //adjust the width for padding as necessary
    //
    while(padWidth%4!=0) {
        padWidth++;
    }
    int offset= padWidth-byteWidth;
    //calculate the size of the image data with padding
    dataSize=(width*height*3)+height*offset;
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

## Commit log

2018-12-26 Update and rename ServoControl2Main.c to ServoControlMain.c
2022-01-29 touch model 3B new board
2022-02-01 recompile slave after wiringpi update
